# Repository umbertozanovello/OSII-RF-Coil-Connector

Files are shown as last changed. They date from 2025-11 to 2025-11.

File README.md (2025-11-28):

# OSI<sup>2</sup> compatible RF Coil Connector
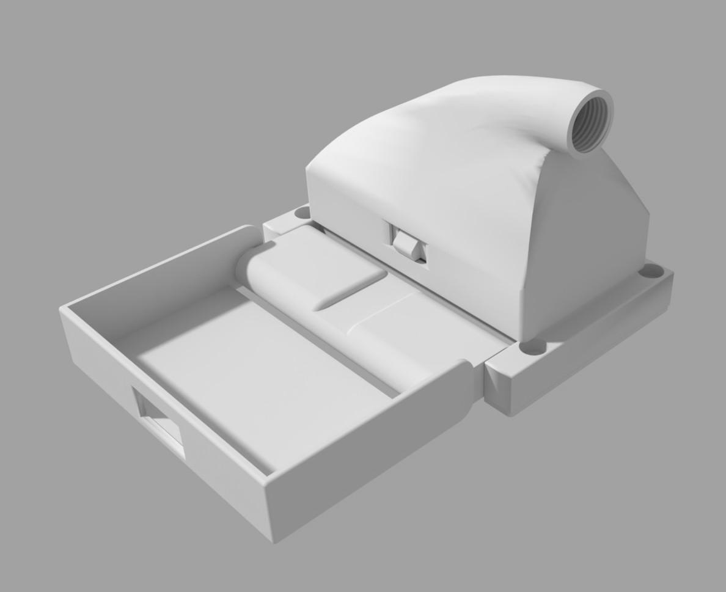
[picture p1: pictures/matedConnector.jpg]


This connector has been primarlily developed to interface with the [OSI<sup>2</sup> MRI LowField scanner](https://www.opensourceimaging.org/project/osii-one/). All the housing is designed to be 3D printed and the electronic boards can be manufactured by standard PCB manufacturing. Production files (e.g., Gerbers, stl, etc.) are provided as assets to the releases.

The last version of this connector features one design for the housing and for the boards. Their characteristics are described in the relevant following sections

## housing1
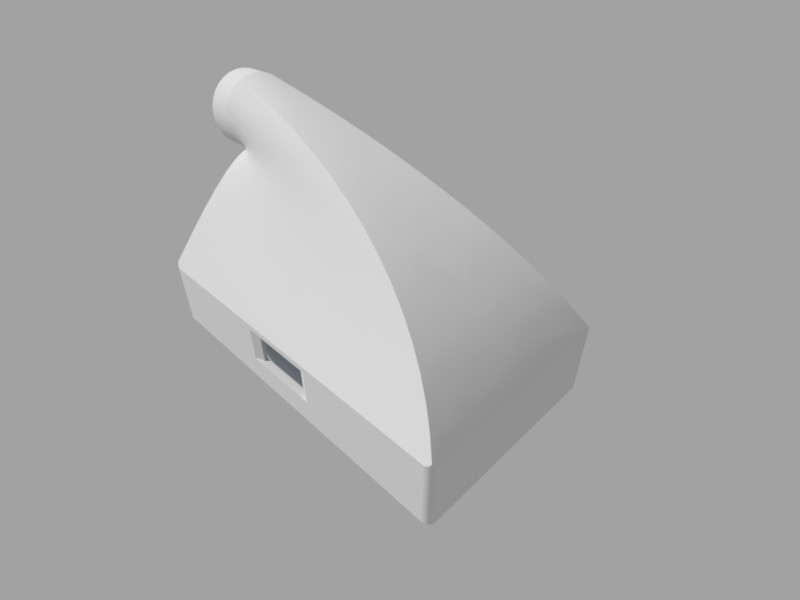
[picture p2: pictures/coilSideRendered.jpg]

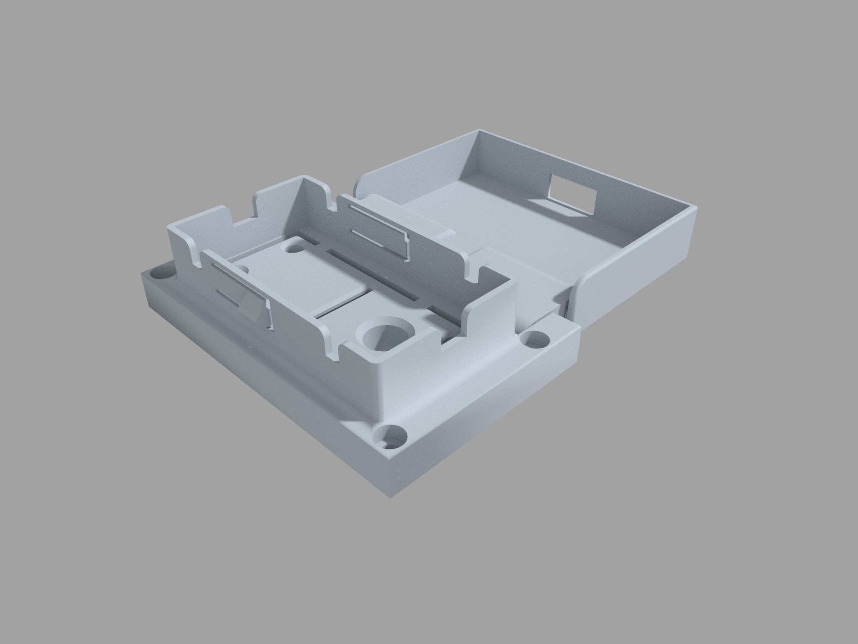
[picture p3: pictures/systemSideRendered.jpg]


This housing is intended for use with one RF coil. Its shape is optimized for being eaily handed by one hand and features a locking mechanism to maintain contact in case of vibrations or minor accidental force on the cable. The system-side component provides a dust cover to protect the exposed circuitry when the RF coil is disconnected. The cover is connected to the main part of the system-side component through a hinge mechanism. The same component is supposed to be mounted on a panel that leaves access to the back part of the connector from where the cables from/to the scanner are connected. The coil-side component of the connector is made of three sub components designed to handle the connector, to secure the electronic boards and to protect the circuitry. Refer to the [assembly guide](docs/assembly-guide.md) for further information.
Four guide pins ensures the correct alignment of the coil- system-side components.

### board1
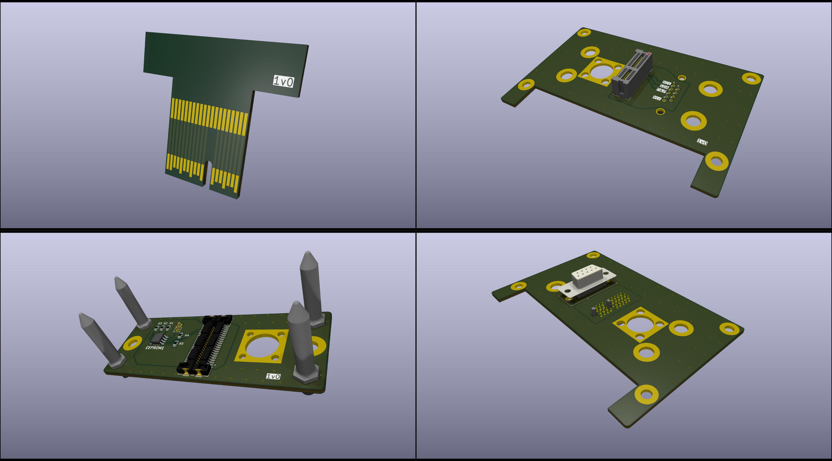
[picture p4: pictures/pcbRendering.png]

This board set features the following characteristics:
- One coaxial channel for Tx/Rx of the MR signal. This is provided by tho BNC-SMA panel adapters. Both the adapters convert a BNC to an SMA female connector supposed to be connected to the RF coil and to the Rx/Tx switch. The BNC female side is standard while the male side is a version without the Bayonet to ensure a "quick push" connection.
- Up to 36 contacts for DC or logic signals provided by an Edge Card connection.
- Implementation of the *Physical Layer* of the [MRCODS Open Standard](https://github.com/umbertozanovello/OpenStandard-CoilID/tree/main) (MRI RF Coil Open Data Standard)
- Electrically separated RF shield and Reference Ground for logical signals
- Logic and DC signals available to the scanner through a female Dsub 9 connector

## Contributors (alphabetical order)

- Nicola De Zanche
- Joshua Harper
- Jack Hayhoe
- Tri Nguyen
- Umberto Zanovello

## LICENSE
This is an open source hardware project licensed under the CERN Open Hardware Licence Version 2 - Weakly Reciprocal. For more information see the [license](./LICENSE-CERN-OHL-W) file

## CITATION
To help users correctly cite your project, a "CITATION.cff" file (read here about [citation files](https://docs.github.com/en/repositories/managing-your-repositorys-settings-and-features/customizing-your-repository/about-citation-files)) is provided with this template and can be modified according to the specific requirements.

## Acknowledgements
The connector has been developed in the framework of the project 22HLT02 A4IM. The project (22HLT02 A4IM) has received funding from the European Partnership on Metrology, co-financed by the European Union's Horizon Europe Research and Innovation Programme and by the Participating States.

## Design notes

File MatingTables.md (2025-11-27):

# Mating Tables

## housing1

| Coil-Side &#8595;| System-Side &#8594;| | | |
|-|-|-|-|-|
| | board1_systemBase | 
board1_coilBase + board1_coilEdgeCard | x

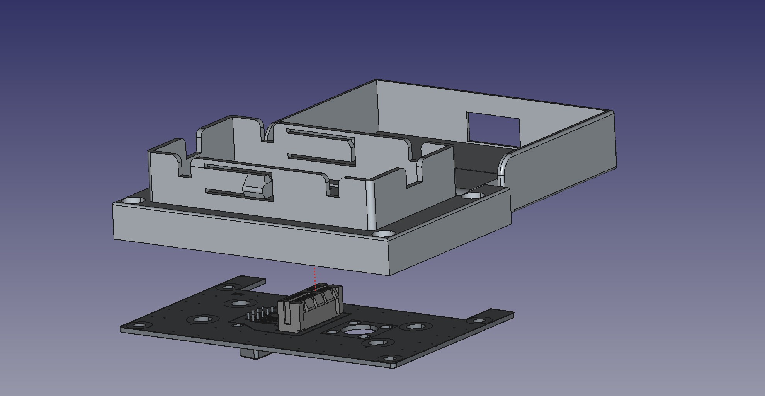
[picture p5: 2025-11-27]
pictures/systemSideExploded.jpg

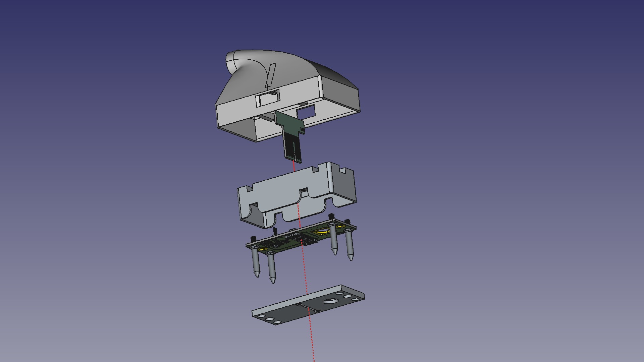
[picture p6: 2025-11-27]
pictures/coilSideExploded.jpg

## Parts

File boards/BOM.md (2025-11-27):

# board1 BOM

| QTY | PART NUMBER | POSSIBLE SOURCE | DESCRIPTION | IDENTIFIER
|-----|-------------|--------|------------|---------
| 1 | 105647 | vcablemart |  BNC Female to SMA Female Panel Jack to Jack Adapter | BNCf-SMAf
| 1 | 105645 | vcablemart |  BNC Male to SMA Female Panel Jack to Jack Adapter (Quick Push)| BNCm-SMAf
| 2 | - | various |  10 kOhm Resistors with 0805 (in) case | 10kR
| 3 | - | various |  0 Ohm Resistors with 0805 (in) case (optional) | 0R
| 1 | - | various |  I2C EEPROM with SOIC-8 case | EEPROM
| 2 | SAL1-120-01-S-S-A-TR | Mouser |  PCIe Socket for PCB PassThrough 20 contacts| PT-PCIe-sock
| 1 | PCIE-036-02-F-D-TH | Mouser |  PCIe Socket for PCB 30 contacts| PCIe-sock
| 1 | 61800929321  | Mouser | D-sub 9 Female Through Hole Connector | Dsub9Conn

**ESTIMATED COST: $ 30 + (board fabrication costs)**

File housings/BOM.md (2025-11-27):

# housing1 BOM

| QTY | PART NUMBER | POSSIBLE SOURCE | DESCRIPTION | IDENTIFIER
|-----|-------------|--------|------------|---------
| 4 | - | Various | M2 Screws, Countersink, L=10 mm | M2-10 Screws
| 4 | - | Various | M3 Screws, L=10 mm | M3-10 Screws
| 6 | - | Various | M4 Screws, L=15 mm | M4-15 Screws
| 4 | 204-0616 | RS Components | M3 Threaded Inserts | M3 Inserts
| 6 | 204-0617 | RS Components | M4 Threaded Inserts | M4 Inserts
| 4 | 571-2239821 | Mouser | M4 Guide Pins | Guide Pins
| 170 g | - | Various | PLA Filament | - 
| 40 g | - | Various | PVA Filament | - 

**ESTIMATED COST: $ 25**

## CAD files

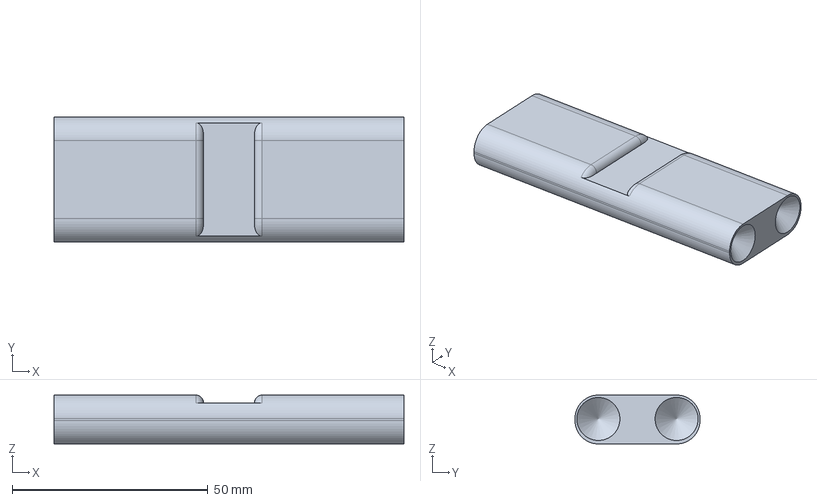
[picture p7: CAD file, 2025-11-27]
housings/housing1_system-side_Hinge.FCStd
89.5 x 32.0 x 12.5 mm

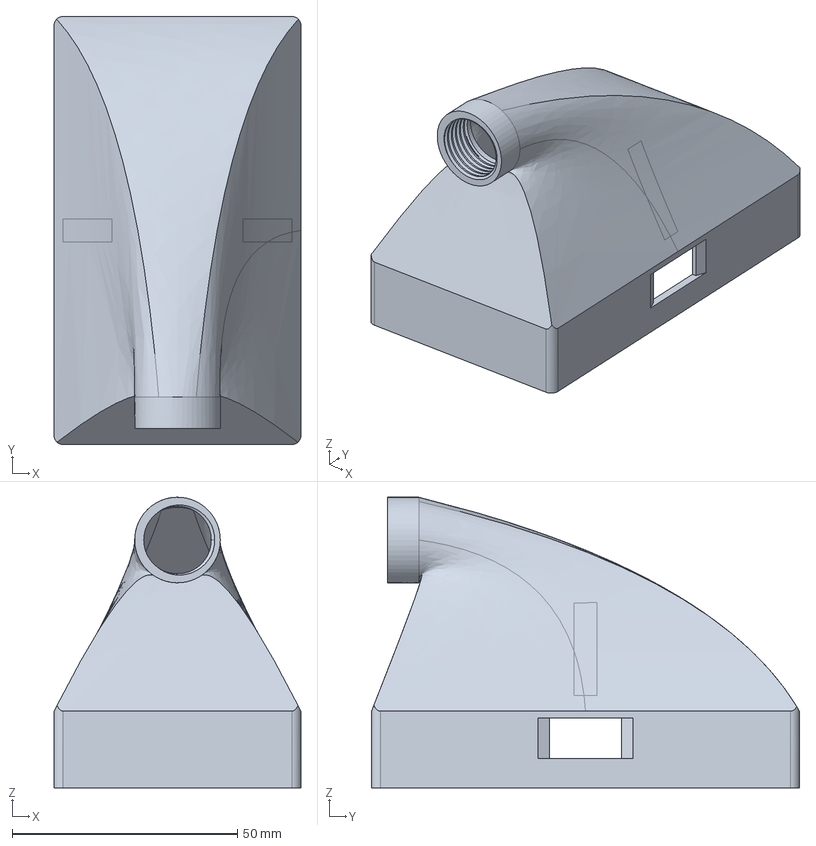
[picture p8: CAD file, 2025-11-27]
housings/housing1_coil-side_TopCover.FCStd
54.8 x 95.0 x 64.5 mm

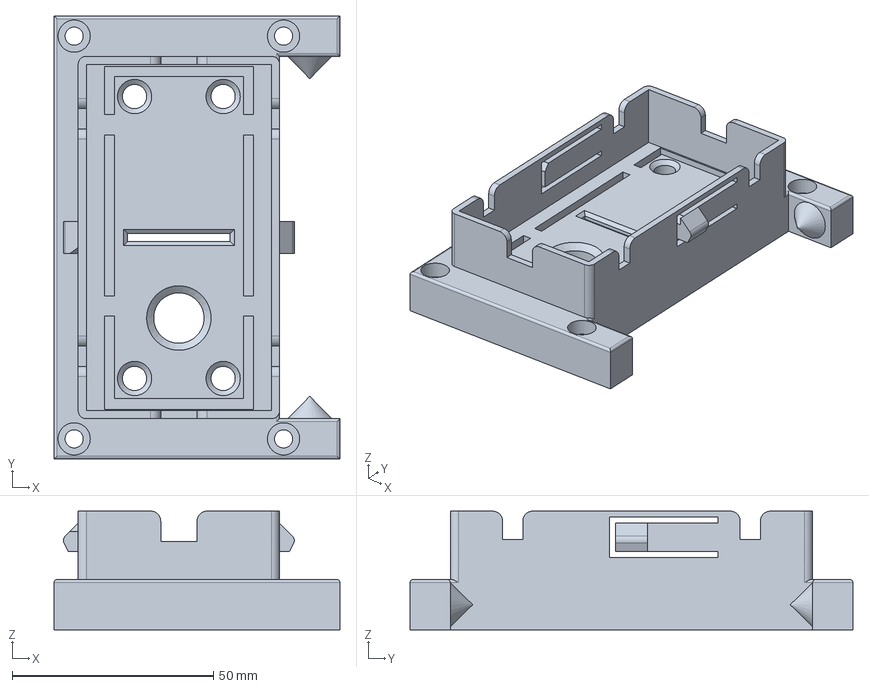
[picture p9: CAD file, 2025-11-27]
housings/housing1_system-side_Base.FCStd
71.0 x 110.0 x 29.5 mm

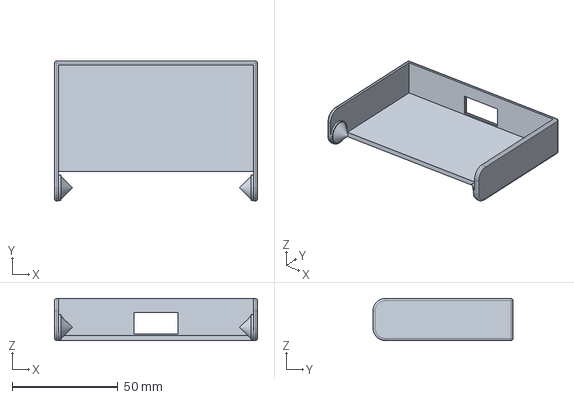
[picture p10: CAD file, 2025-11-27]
housings/housing1_system-side_DustCover.FCStd
96.0 x 66.2 x 20.0 mm

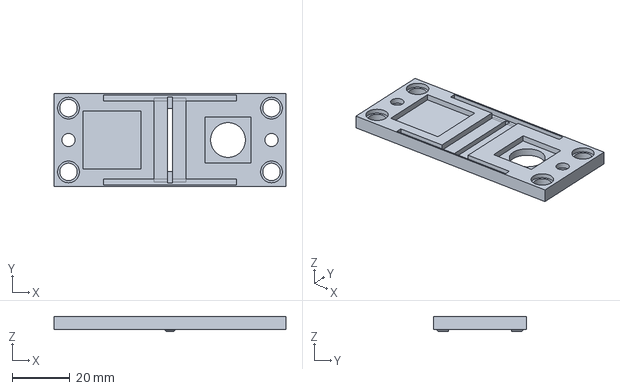
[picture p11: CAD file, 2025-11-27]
housings/housing1_coil-side_CentrePiece.FCStd
80.0 x 32.0 x 5.25 mm

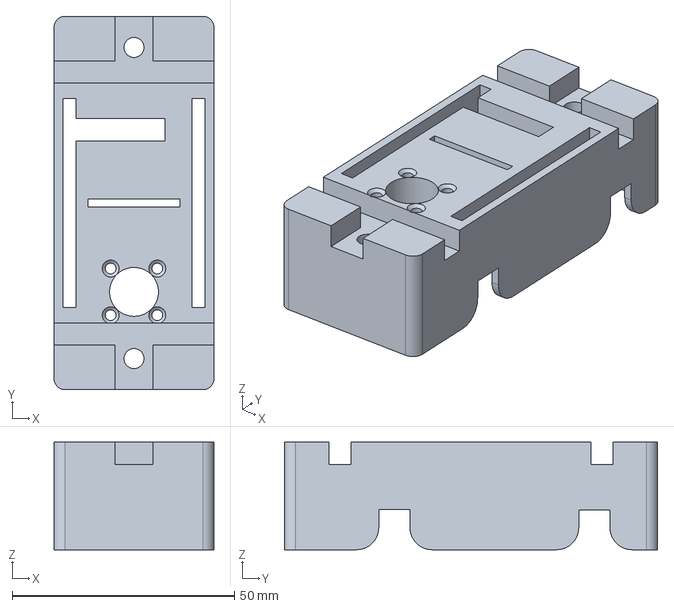
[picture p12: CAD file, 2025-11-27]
housings/housing1_coil-side_TopPiece.FCStd
36.0 x 84.0 x 24.2 mm

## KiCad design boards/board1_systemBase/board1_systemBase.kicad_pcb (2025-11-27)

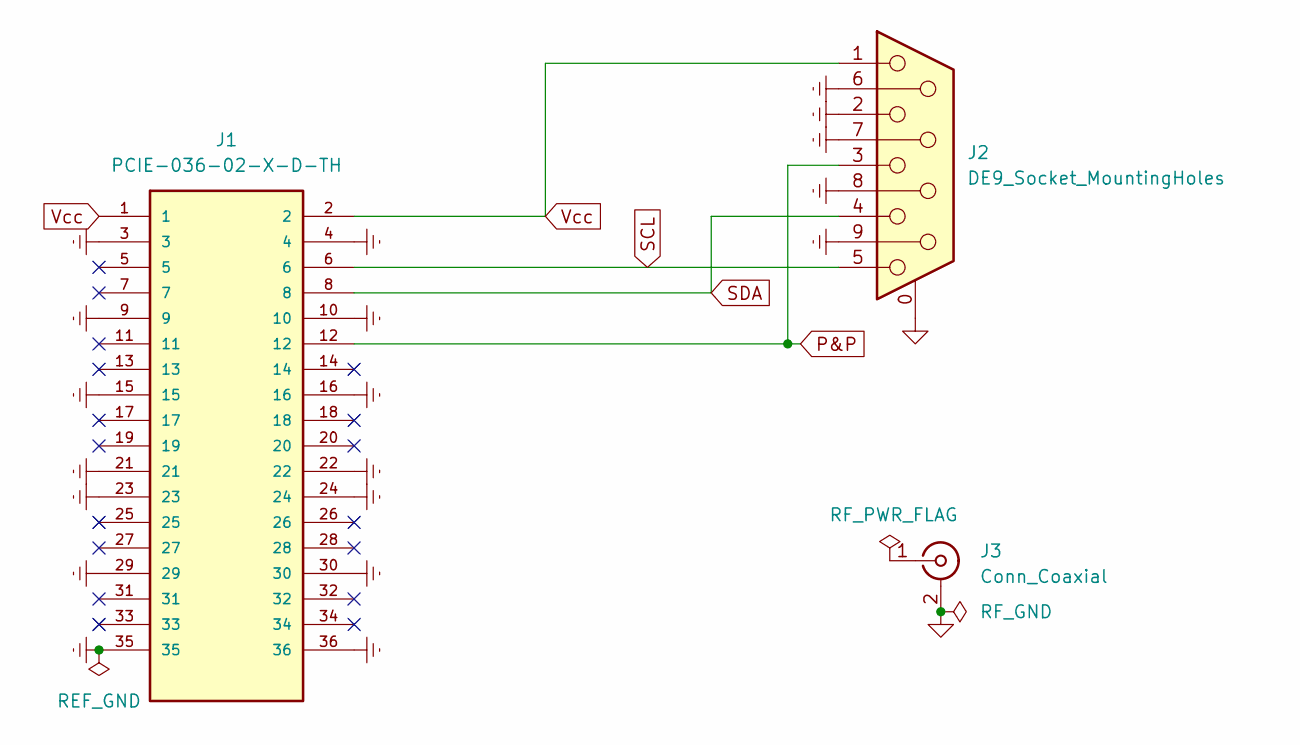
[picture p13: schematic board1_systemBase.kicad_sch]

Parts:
J1: PCIE-036-02-X-D-TH; SAMTEC_PCIE-036-02-X-D-TH; Manufacturer Part Number PCIE-036-02-F-D-TH; Mouser Part Number 200-PCIE03602FDTH
J2: DE9_Socket_MountingHoles; DSUB-9_Socket_Vertical_P2.77x2.84mm_MountingHoles; Manufactuer Part Number 61800929321; Mouser Part Number 710-61800929321
J3: Conn_Coaxial; femaleBNCPanel

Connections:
GNDREF: J1.3, J1.4, J1.9, J1.10, J1.15, J1.16, J1.21, J1.22, J1.23, J1.24, J1.29, J1.30, J1.35, J1.36, J2.2, J2.6, J2.7, J2.8, J2.9
GNDRF: J2.0 (PAD), J3.2 (Ext)
P&P: J1.12, J2.3
SCL: J1.6, J2.5
SDA: J1.8, J2.4
Vcc: J1.1, J1.2, J2.1

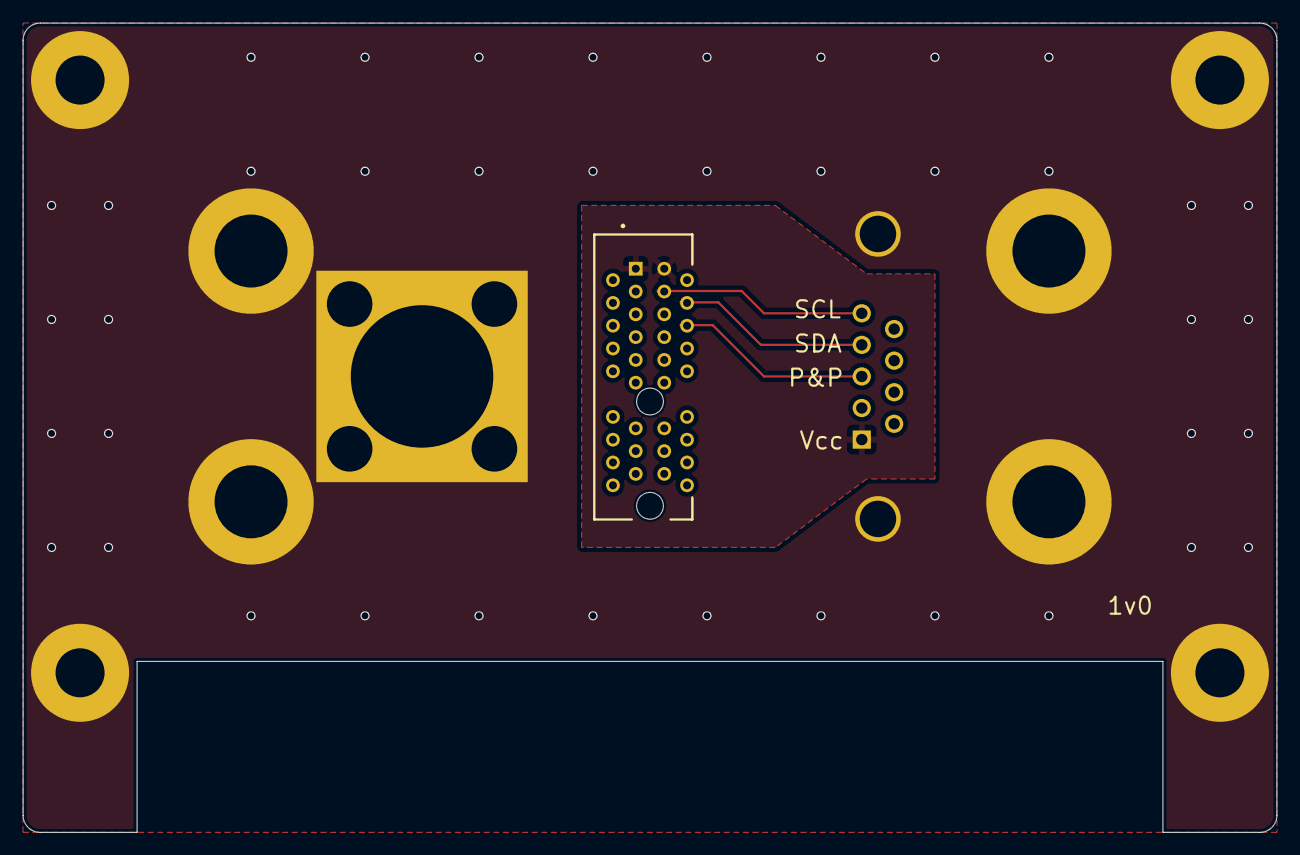
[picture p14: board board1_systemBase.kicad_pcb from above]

Board: 2 copper layers, 110.0 x 71.0 mm, 3 parts (1 on the bottom side), 6 nets.

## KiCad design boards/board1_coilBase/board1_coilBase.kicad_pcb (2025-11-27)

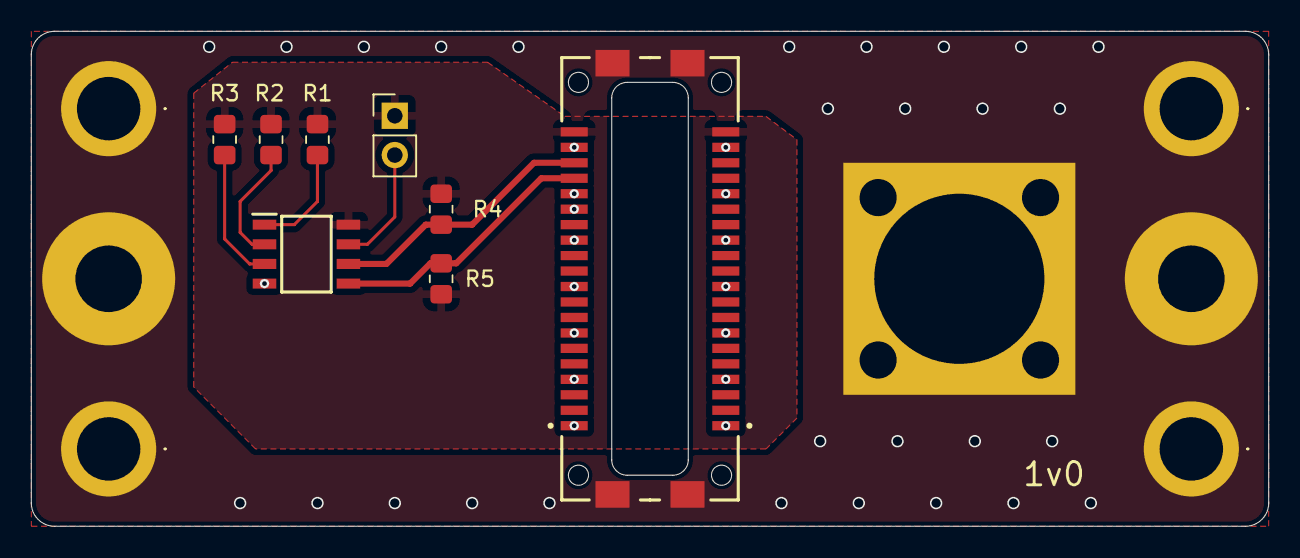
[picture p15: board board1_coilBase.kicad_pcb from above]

Board: 2 copper layers, 80.0 x 32.0 mm, 13 parts (0 on the bottom side), 9 nets.

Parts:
EEPROM1: M24C01-RMN6P; SOIC8
J1: Double_SAL1-120-01-XX-S-A; Double_SAMTEC_SAL1-120-01-XX-S-A
J3: Conn_Coaxial; maleBNCPanel
J4: Conn_01x02_Pin; PinHeader_1x02_P2.54mm_Vertical
J**: 2239821
J**#2, J**#3, J**#4: 2239821
R1, R2, R3: 0R0; R_0805_2012Metric_Pad1.20x1.40mm_HandSolder
R4, R5: 10k0; R_0805_2012Metric_Pad1.20x1.40mm_HandSolder

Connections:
GNDREF: EEPROM1.4 (VSS), J1.3, J1.4, J1.9, J1.10, J1.12, J1.15, J1.16, J1.21, J1.22, J1.27, J1.28, J1.33, J1.34, J1.39, J1.40
GNDRF: J1.S1 (SHIELD), J1.S2 (SHIELD__1), J1.S3 (SHIELD), J1.S4 (SHIELD__1), J3.2 (Ext), J**.1, J**#2.1, J**#3.1, J**#4.1
unnamed: EEPROM1.1 (E0), R1.1
unnamed: EEPROM1.2 (E1), R2.1
unnamed: EEPROM1.3 (E2), R3.1
unnamed: EEPROM1.7 (~WC), J4.2
SCL: EEPROM1.6 (SCL), J1.6, R4.1
SDA: EEPROM1.5 (SDA), J1.8, R5.1
Vcc: EEPROM1.8 (VCC), J1.1, J1.2, J4.1, R1.2, R2.2, R3.2, R4.2, R5.2
